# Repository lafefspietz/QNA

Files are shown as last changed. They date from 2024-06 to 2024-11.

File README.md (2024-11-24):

# [Quantum Network Analyzer](https://github.com/lafefspietz/QNA/)

System for calibrated high throughput microwave scattering parameter measurement using quantum standards.

Microwave lines are expensive.  Dil fridges are expensive.  Adding cryogenic RF switches to a system can be a force multiplier for both microwave measurement infrastructure and cryogenic infrastructure, multiplying up the number of chips which can be measured per cool down by however many RF lines the switch network adds. 

The system documented here turns one RF line into 9 by taking a single RF input, using switches to split between 9 quantum samples, and then a second switch network which feeds a single RF output. A mechanical assembly with COTS cryogenic RF devices will allow for measuring all 4 scattering parameters with a single RF in and RF output.  

Calibration software which can use a standard qubit chip to measure test chips will be part of the system.  An Arduino-based rack mount controller is part of the system as well.

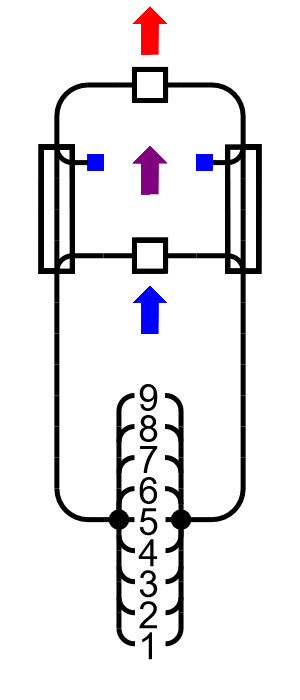
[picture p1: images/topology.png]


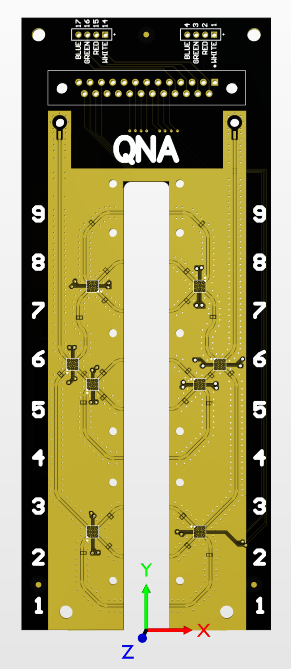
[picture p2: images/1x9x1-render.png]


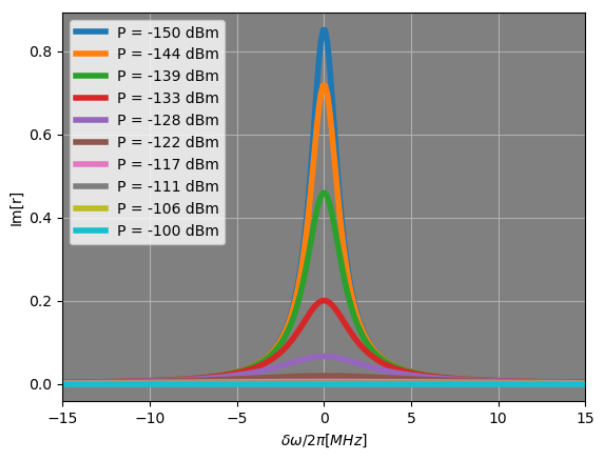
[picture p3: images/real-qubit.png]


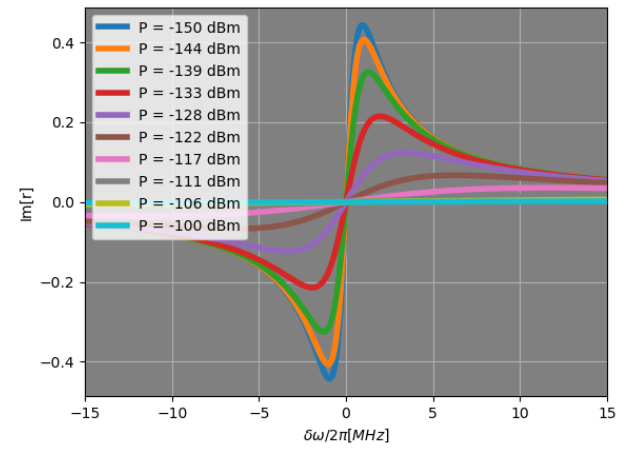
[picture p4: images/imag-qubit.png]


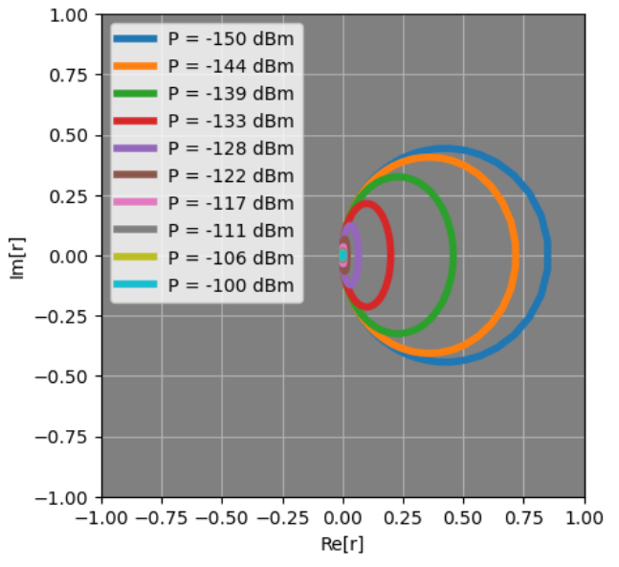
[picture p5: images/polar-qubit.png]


## System Elements

 - Wood board to fit in 19 inch rack
 - Control panel circuit board
 - 3d printed parts to connect circuit boards to wood board
 - Custom machined aluminum box to contain 90 volt electronics
 - DSUB to Fischer cable to connect to dil fridge
 - Arduino Mega 
 - Arduino Mega shield circuit board and components
 - DC DC converter built from COTS circuits
 - Relay control board with pull down resistors which selects which DC lines are energized with 90 volts
 - 1x9x1 switch board which puts 9 quantum devices in a single cryogenic RF line
 - Mounting bracket for COTS cryogenic RF components
 - Collection of COTS cryogenic RF components which bold to the above bracket
 - Sample enclosure
 - Outer sample box lid with small opening for changing samples and wire bonding
 - Inner sample box lid over sample opening
 - Standard qubit chips of different sizes
 - Arduino control code
 - Python control code
 - Calibration method based on tunable qubit chips to determine both scattering parameter calibration and noise calibration

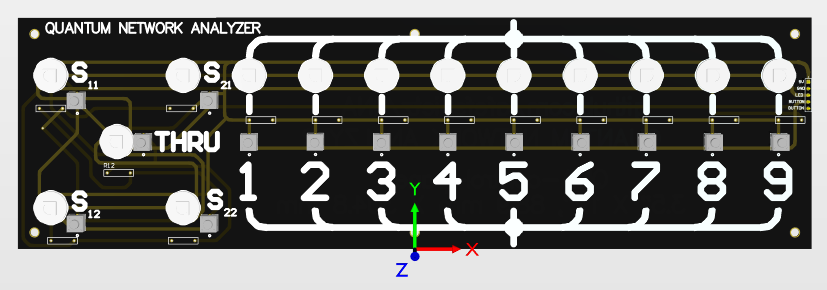
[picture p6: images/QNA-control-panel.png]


 - [14X pixels Flora RGB Smart NeoPixel version 3 - Sheet of 20](https://www.adafruit.com/product/1559)
 - [14X SPST tactile switch, E-Switch part number TL59NF160Q](https://www.digikey.com/en/products/detail/e-switch/TL59NF160Q/390533)
 - [1X 5 wire cables](https://www.amazon.com/StarTech-USBINT5PIN-Internal-Motherboard-Header/dp/B003HHROBG/)
 - [14X 10 k 0.1% axial reistors, Yageo part number MFP-25BRD52-10K](https://www.digikey.com/en/products/detail/yageo/MFP-25BRD52-10K/2058797)

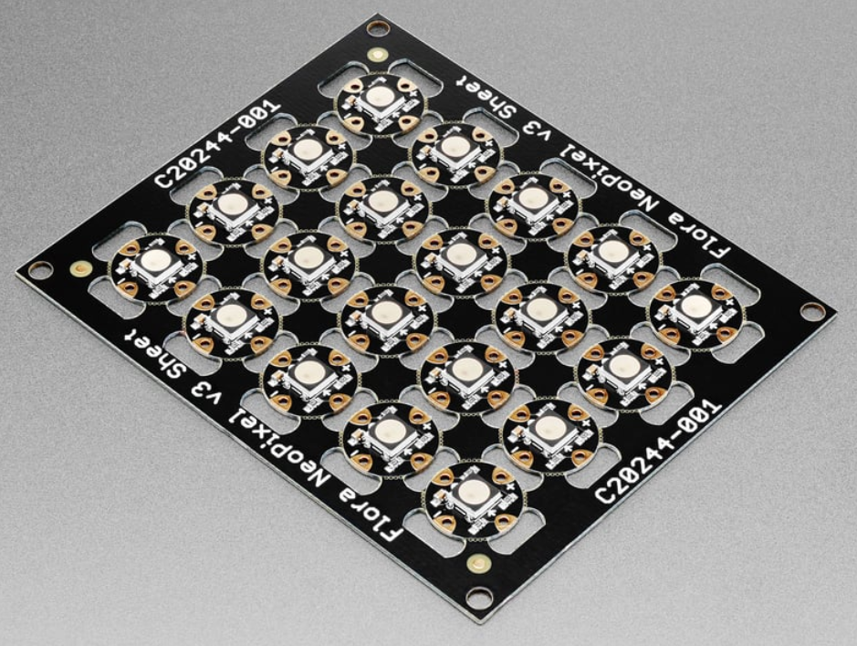
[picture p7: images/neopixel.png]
(https://www.adafruit.com/product/1559)


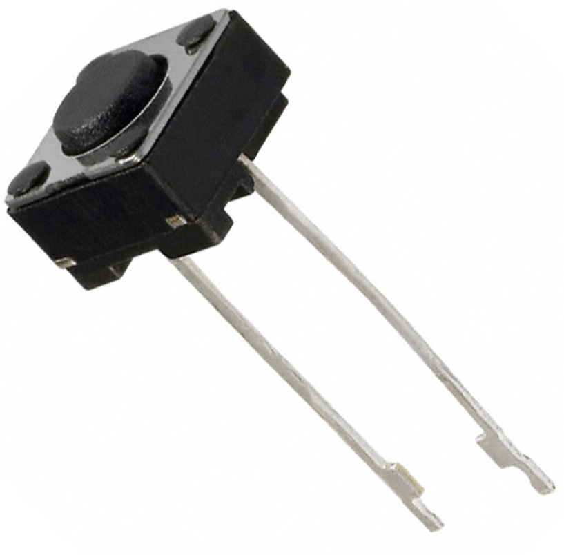
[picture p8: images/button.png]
(https://www.digikey.com/en/products/detail/e-switch/TL59NF160Q/390533)


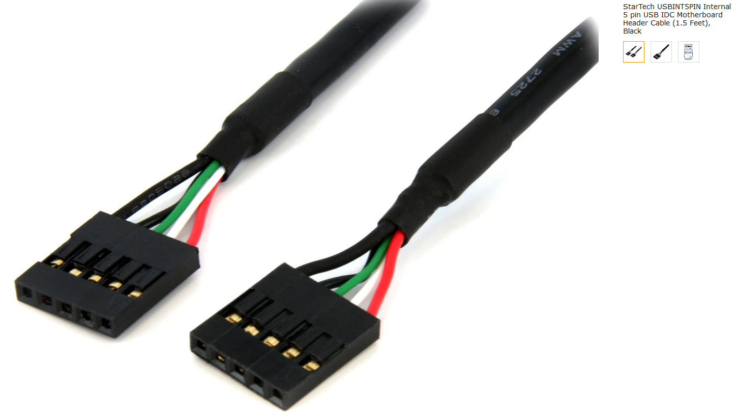
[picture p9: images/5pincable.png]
(https://www.amazon.com/StarTech-USBINT5PIN-Internal-Motherboard-Header/dp/B003HHROBG/)


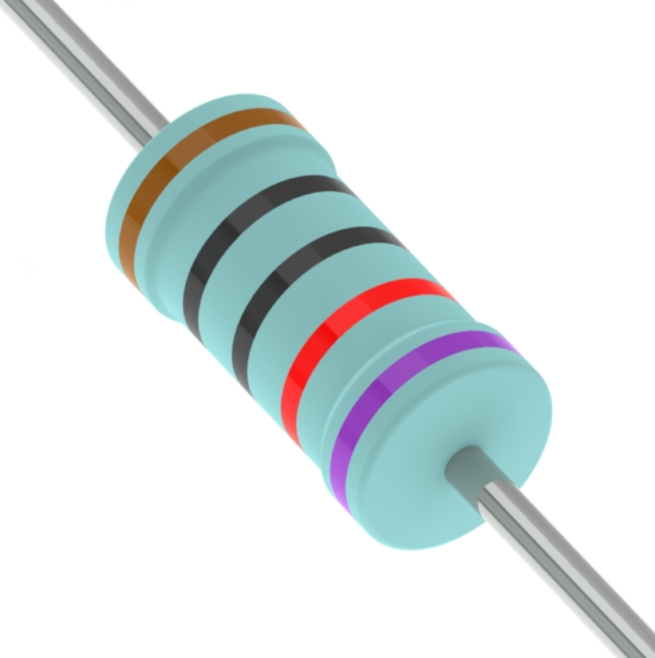
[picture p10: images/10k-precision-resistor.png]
(https://www.digikey.com/en/products/detail/yageo/MFP-25BRD52-10K/2058797)


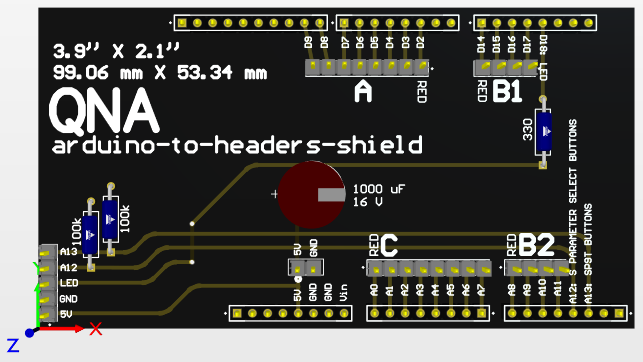
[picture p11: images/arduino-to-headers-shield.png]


 - [arduino-to-headers-shield-gerberes.zip](arduino-to-headers-shield-gerberes.zip)
 - [1000 uF 16 V electrolytic capacitor, Rubycon part number 16PK1000MEFC10X12.5](https://www.digikey.com/en/products/detail/rubycon/16PK1000MEFC10X12-5/3563556)
 - [100 kOhm Stackpole Electronics part number RNF14FTD100K](https://www.digikey.com/en/products/detail/stackpole-electronics-inc/RNF14FTD100K/1706591)
 - [330 Ohm Stackpole Electronics part number CF18JT330R](https://www.digikey.com/en/products/detail/stackpole-electronics-inc/CF18JT330R/1741683)
 - [0.1 inch header strips](https://www.amazon.com/Header-Lystaii-Pin-Connector-Electronic/dp/B06ZZN8L9S/)

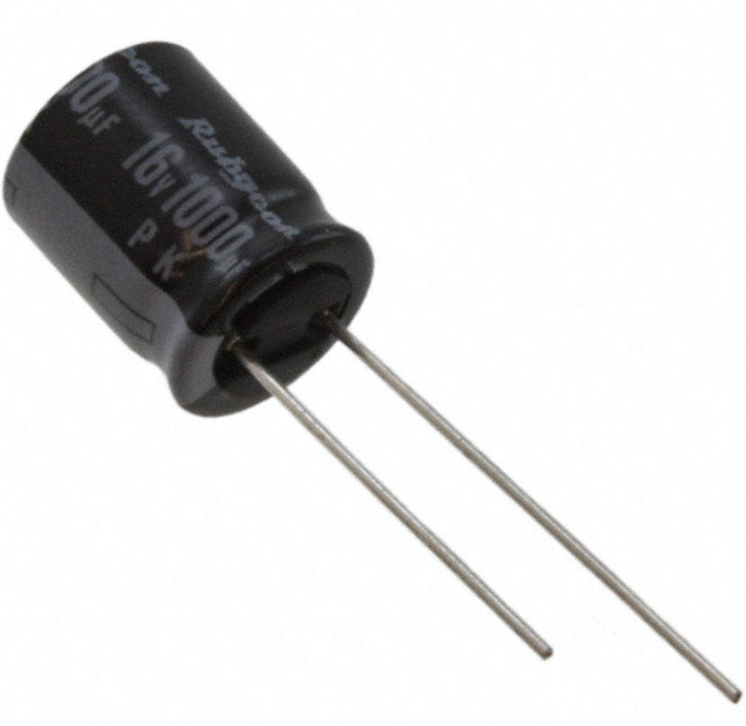
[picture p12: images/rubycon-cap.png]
image of electrolytic capacitor (https://www.digikey.com/en/products/detail/rubycon/16PK1000MEFC10X12-5/3563556)


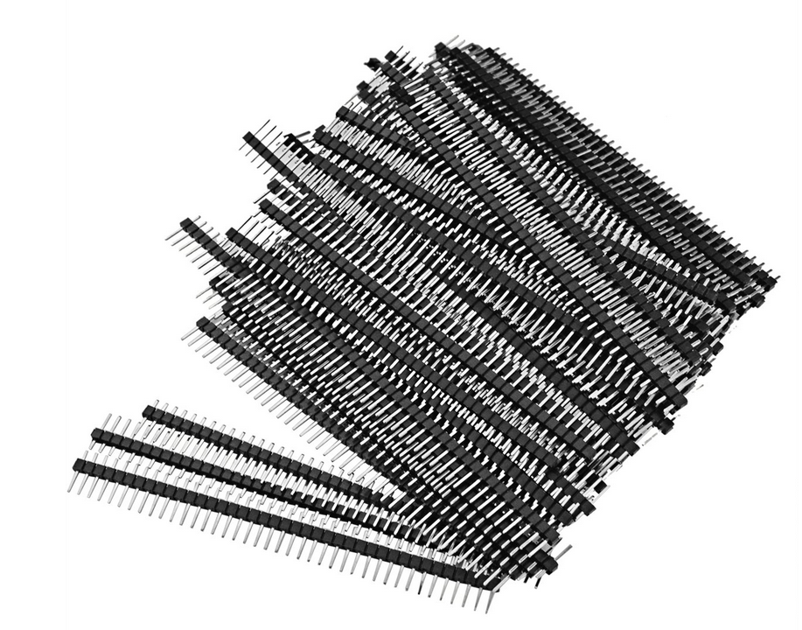
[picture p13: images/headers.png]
[]

Add link here to the 4 and 8 pin cables which connect these boards

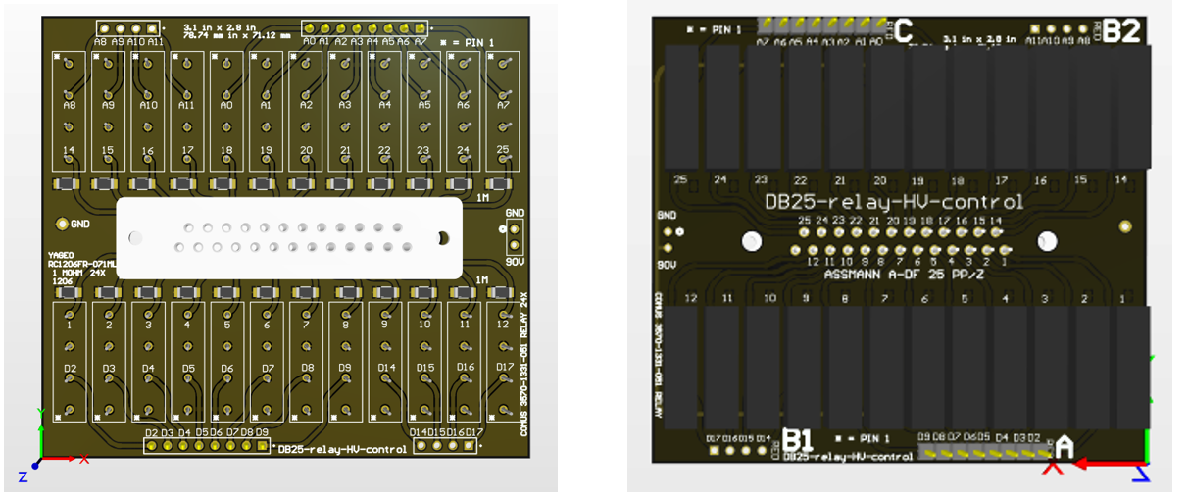
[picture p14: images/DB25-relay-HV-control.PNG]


 - [DB25-relay-HV-control-gerbers.zip](DB25-relay-HV-control-gerbers.zip)
 - [DB25-relay-HV-control-gerbers.PcbDoc](DB25-relay-HV-control-gerbers.PcbDoc)
 - [DB25-relay-HV-control-gerbers.PrjPcb](DB25-relay-HV-control-gerbers.PrjPcb)
 - [DB25-relay-HV-control-gerbers.](DB25-relay-HV-control-gerbers.PrjPcbStructure)
 - [DB25-relay-HV-control-gerbers.](DB25-relay-HV-control-gerbers.SchDoc)
 - [24 x 5 volt relay, Comus International part number 3570-1331-053](https://www.digikey.com/en/products/detail/comus-international/3570-1331-053/7497099)
 - [24x 1 MOhm resistor in SMT 1206 package, Yageo part number RC1206FR-071ML](https://www.digikey.com/en/products/detail/yageo/RC1206FR-071ML/728388)
 - [1x Board mount female DB-25 connector, Assmann part number A-DF 25 PP/Z](https://www.digikey.com/en/products/detail/assmann-wsw-components/A-DF-25-PP-Z/1241794)
 - [0.1 inch header strips](https://www.amazon.com/Header-Lystaii-Pin-Connector-Electronic/dp/B06ZZN8L9S/)

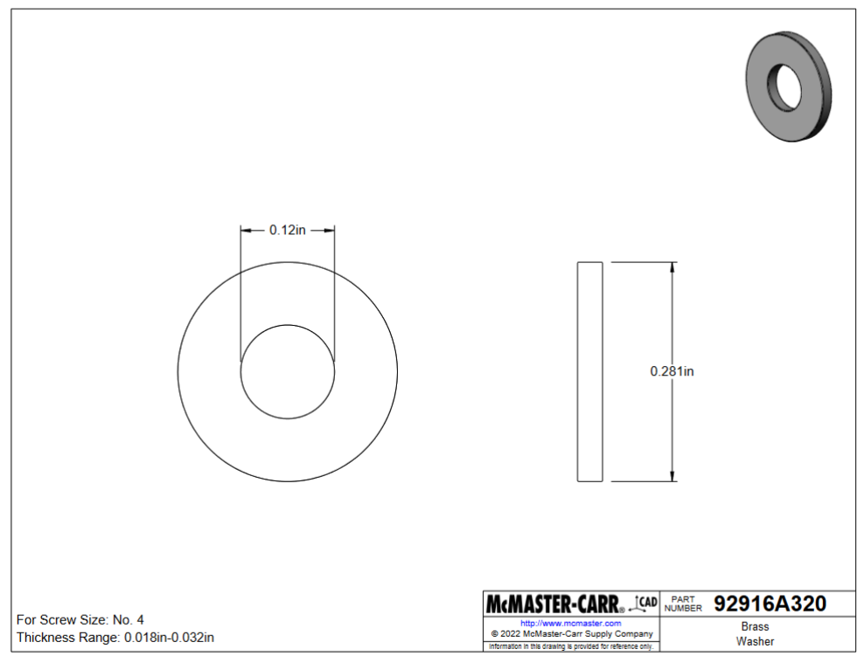
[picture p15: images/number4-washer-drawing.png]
(https://www.mcmaster.com/92916a320/)


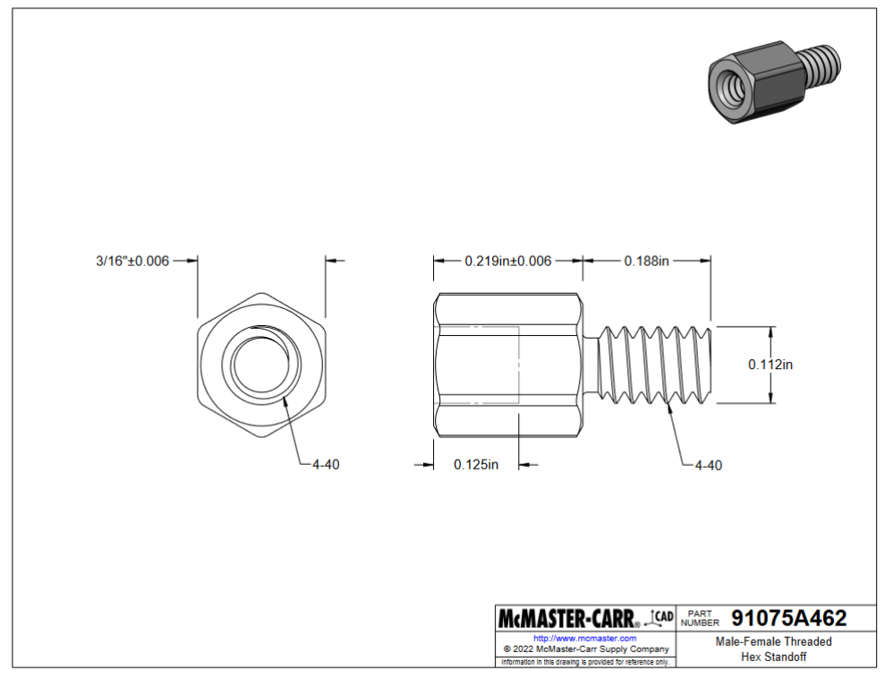
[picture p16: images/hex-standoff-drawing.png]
(https://www.mcmaster.com/91075A462/)


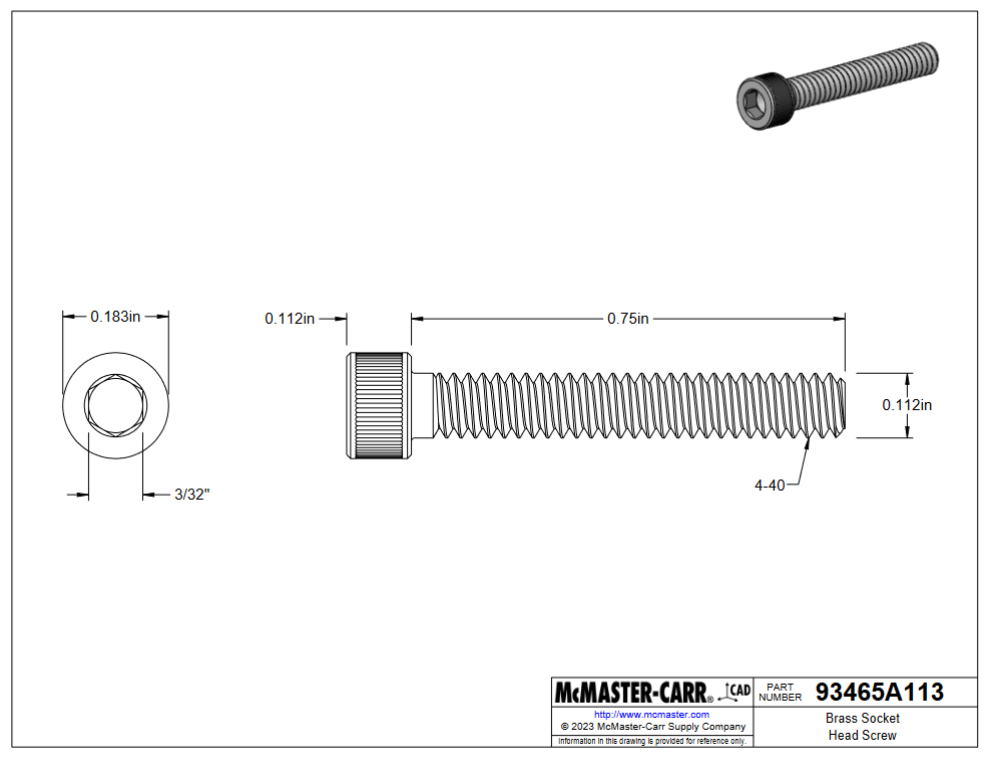
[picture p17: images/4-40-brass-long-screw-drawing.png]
(https://www.mcmaster.com/93465a113/)


# 1x9x1



 - [microd](https://www.digikey.com/en/products/detail/cinch-connectivity-solutions/M83513-25-D01CP/12471446)
 - [2 mm headers](https://www.digikey.com/en/products/detail/te-connectivity-amp-connectors/2-292161-4/5124519)
 - [MEMS switch](https://www.mouser.com/new/menlo-micro/menlo-micro-mm5130-sp4t-rf-switch/)
 - [56 k resistor](https://www.digikey.com/en/products/detail/te-connectivity-passive-product/CPF0201B56K2E1/14007085)
 - [SMP connectors from Molex](https://www.digikey.com/en/products/detail/molex/0853050232/2421464)

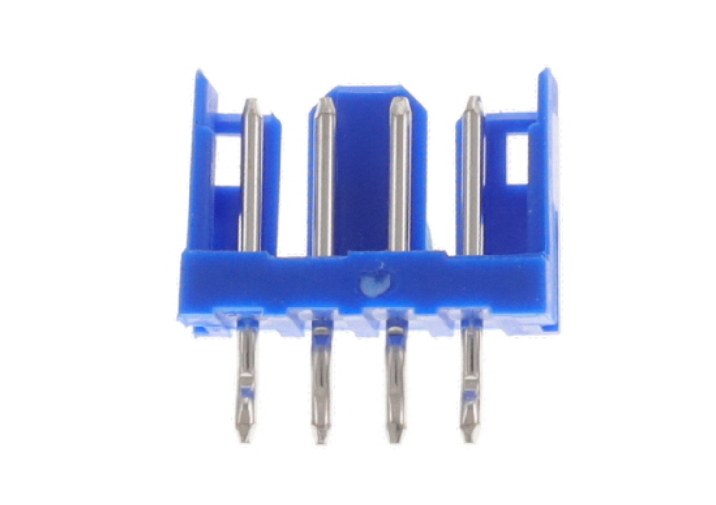
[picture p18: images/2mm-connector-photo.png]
2mm 4 pin connector (https://www.digikey.com/en/products/detail/te-connectivity-amp-connectors/2-292161-4/5124519)


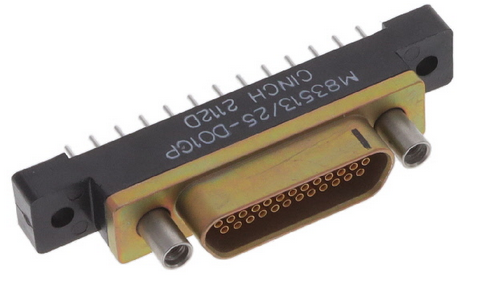
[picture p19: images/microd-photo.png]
(https://www.digikey.com/en/products/detail/cinch-connectivity-solutions/M83513-25-D01CP/12471446)


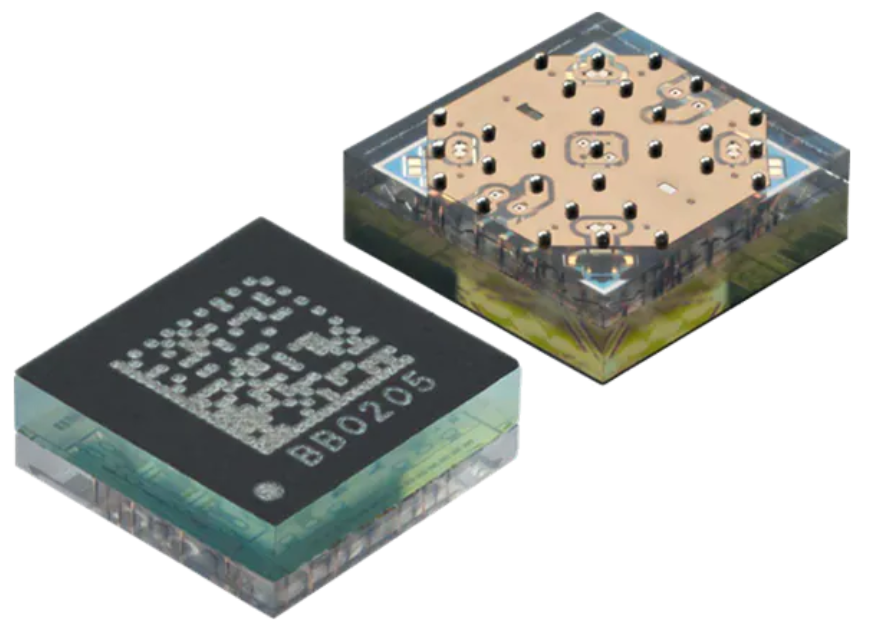
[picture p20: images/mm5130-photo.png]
(https://www.mouser.com/new/menlo-micro/menlo-micro-mm5130-sp4t-rf-switch/)


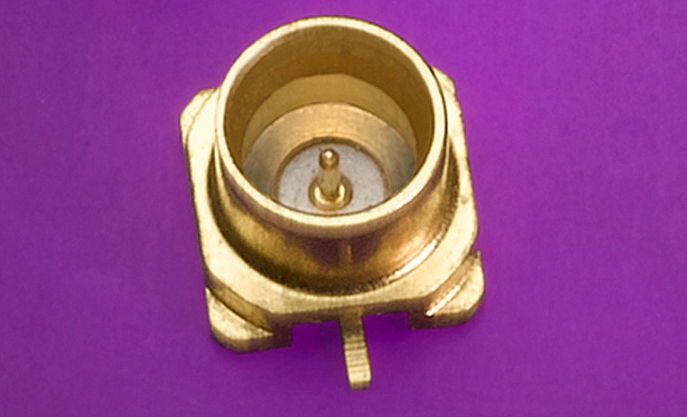
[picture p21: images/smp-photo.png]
(https://www.digikey.com/en/products/detail/molex/0853050232/2421464)


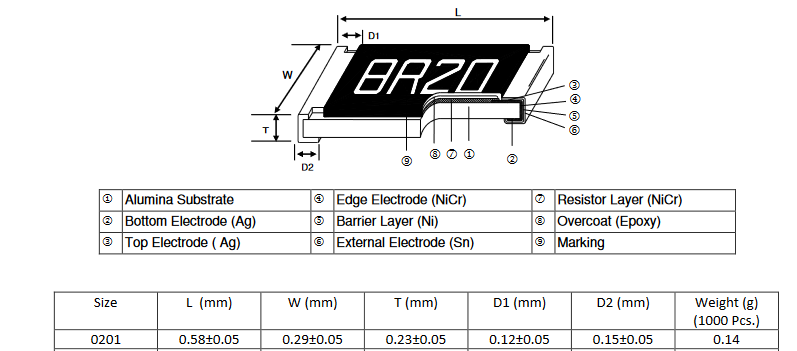
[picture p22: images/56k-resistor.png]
(https://www.digikey.com/en/products/detail/te-connectivity-passive-product/CPF0201B56K2E1/14007085)


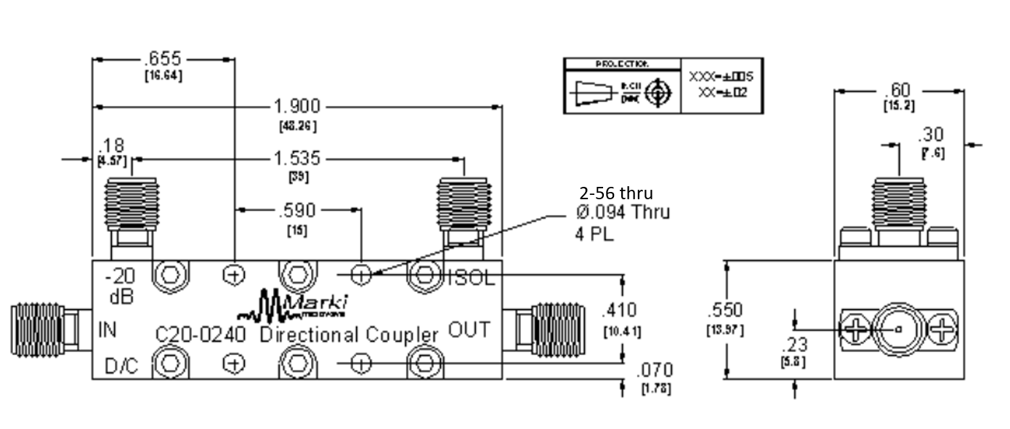
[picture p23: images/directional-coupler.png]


### [Marki Microwave C20-0240 Directional Coupler](https://markimicrowave.com/products/connectorized/directional-couplers/c20-0240/)

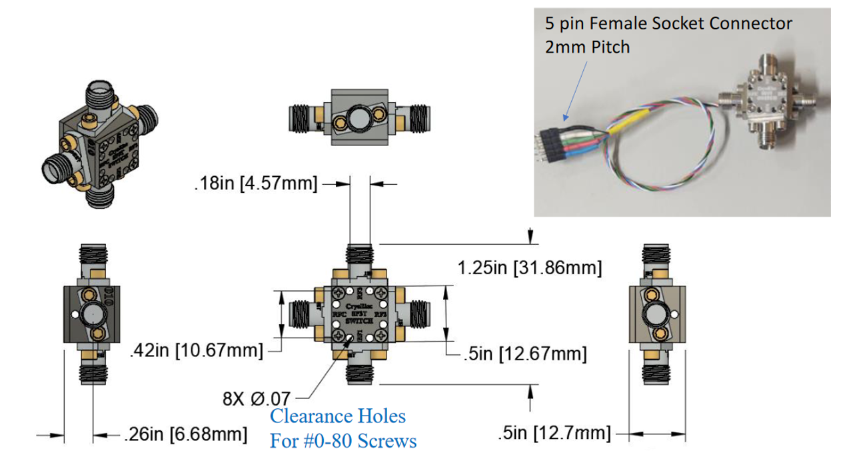
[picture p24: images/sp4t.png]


### [CryoElec SP3T coaxial switch](https://www.cryoelec.com/products/cryoswitchsp3t)

Versions can be constructed for 5 mm chips, 5.06 mm chips, 7.5 mm chips, 10 mm chips, and SMP connectors to break out to external devices.

Install [xampp](https://www.apachefriends.org/).

Install [Anaconda](https://docs.anaconda.com/anaconda/install/)

Open an anaconda prompt and type the following 

```
jupyter notebook --notebook-dir=c:\xampp\htdocs\quantumswitch
```

## 1x9x1 System Elements



### 1x9x1 PCB, RF Pool with RO4350

### [Eurocircuits RF Pool link](https://www.eurocircuits.com/pcb-assembly-rf-pool/)



## 2X

### [TE Connectivity 2-292161-4 CONN HEADER VERT 4POS 2MM](https://www.digikey.com/en/products/detail/te-connectivity-amp-connectors/2-292161-4/5124519)



## 2X

### [Molex 085305-0232 SMT SMP connector](https://www.digikey.com/en/products/detail/molex/0853050232/2421464)



## 1X

### [Cinch Connectivity Solutions M83513/25-D01CP 25 pin microD board mount connector](https://www.digikey.com/en/products/detail/cinch-connectivity-solutions/M83513-25-D01CP/12471446)



## 8X

### [Menlo Micro MM5130-03NDB-TR RF Switch ICs DC-26GHz - SP4T - 2.5 mm x 2.5 mm 29 pin](https://mou.sr/4fuziKD)



### 24X

### [TE Connectivity CPF0201B56K2E1  56 k Ohm 0201 surface mount resistor](https://www.digikey.com/en/products/detail/te-connectivity-passive-product/CPF0201B56K2E1/14007085)

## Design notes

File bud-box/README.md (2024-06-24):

## [Back to Main QNA](../)

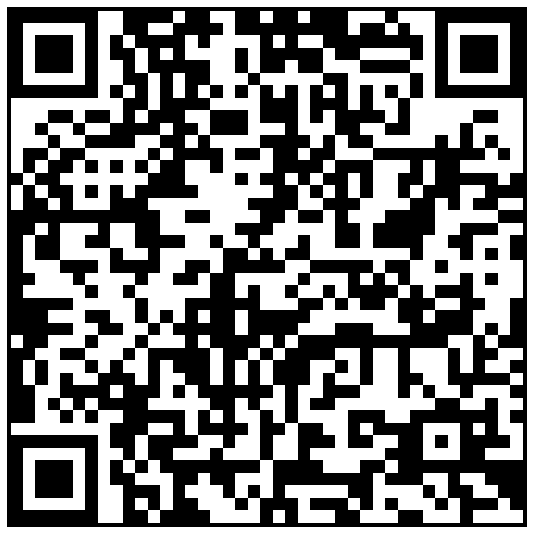
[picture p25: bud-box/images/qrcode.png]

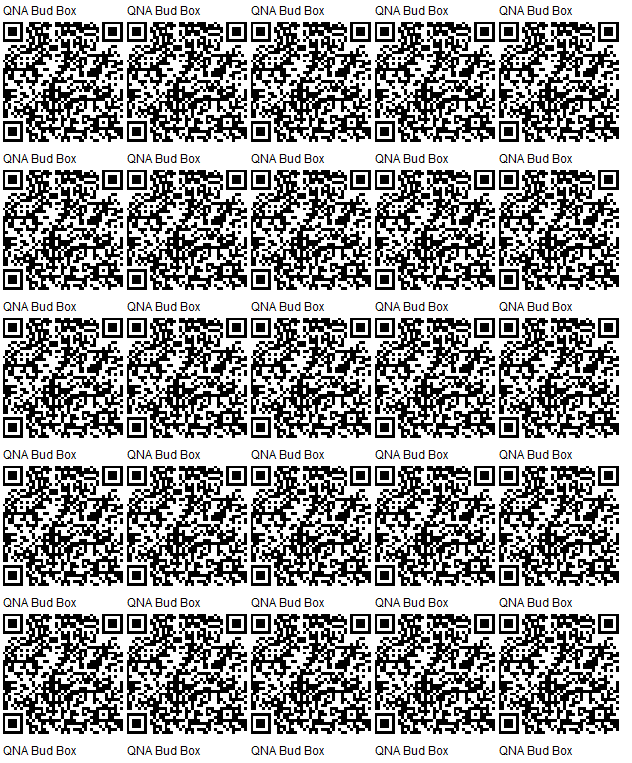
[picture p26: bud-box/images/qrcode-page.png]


# [Bud Box](https://github.com/lafefspietz/QNA/tree/main/bud-box)

We use a diecast aluminum enclosure from [Bud Industries](https://www.budind.com/)(part number [AN-1304-A](https://www.budind.com/product/nema-ip-rated-boxes/an-a-series-style-a-aluminum-enclosure/an-1304/)) to enclose the high voltage driver for the MEMS switches used in the QNA system. 

This box can be modified yourself if you have access to a milling machine or you can get it modified by Bud or by some third party machine shop.  

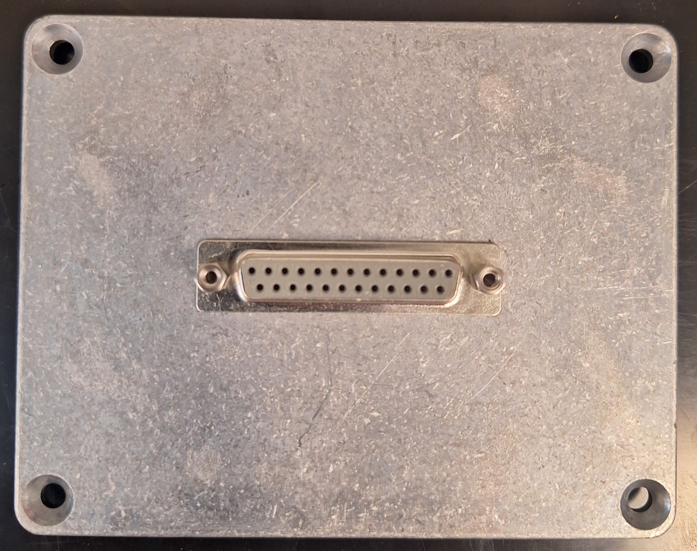
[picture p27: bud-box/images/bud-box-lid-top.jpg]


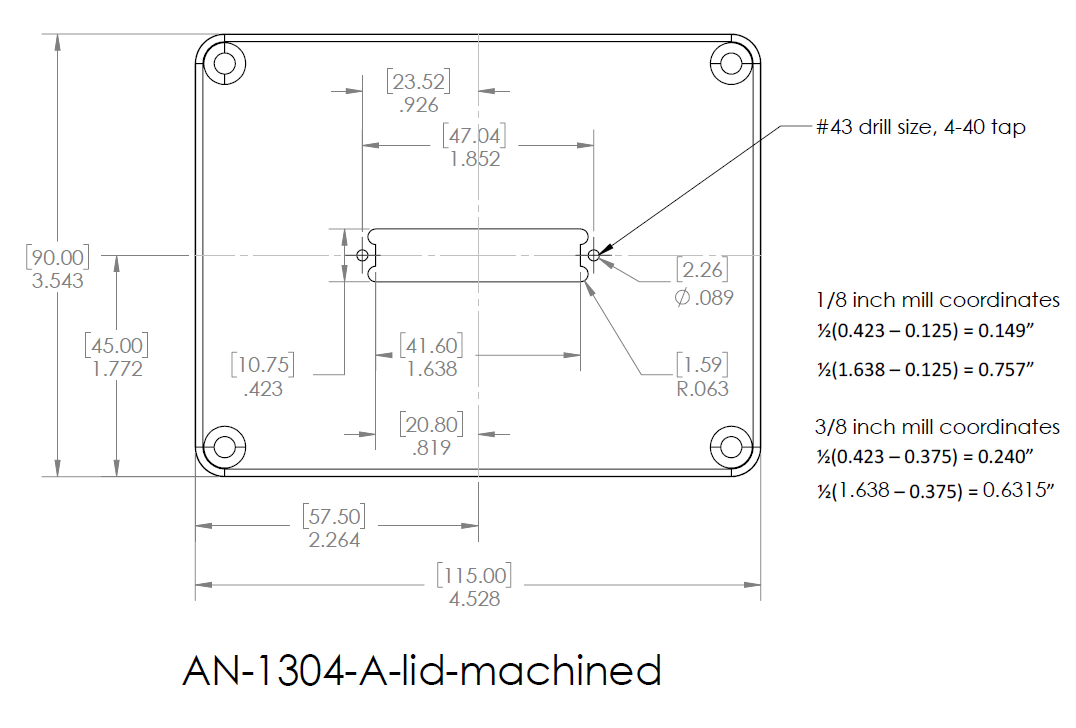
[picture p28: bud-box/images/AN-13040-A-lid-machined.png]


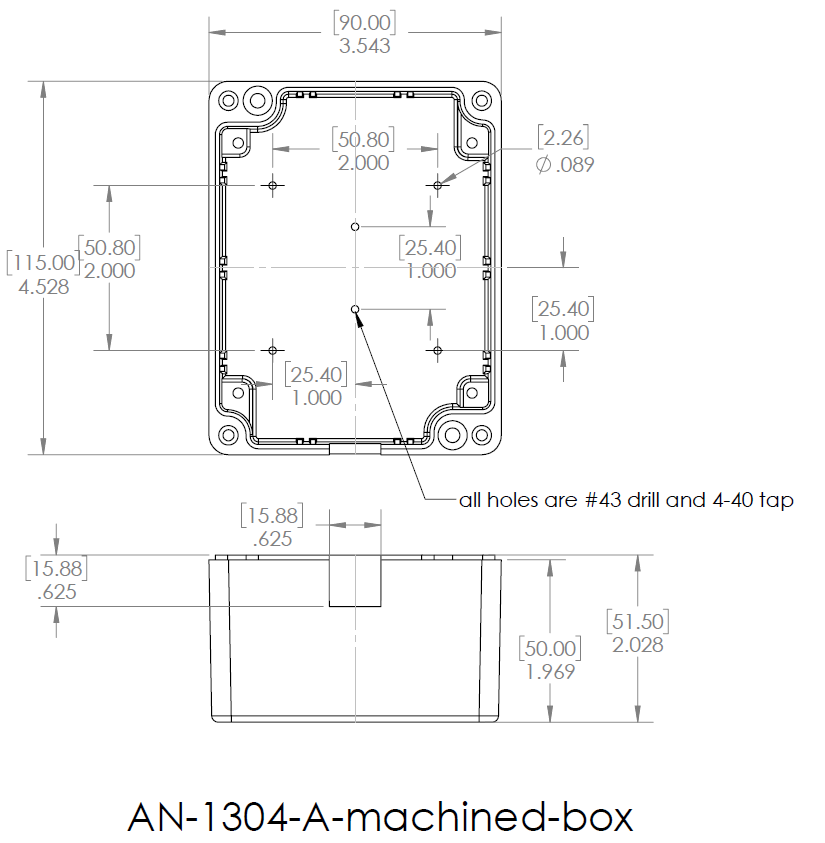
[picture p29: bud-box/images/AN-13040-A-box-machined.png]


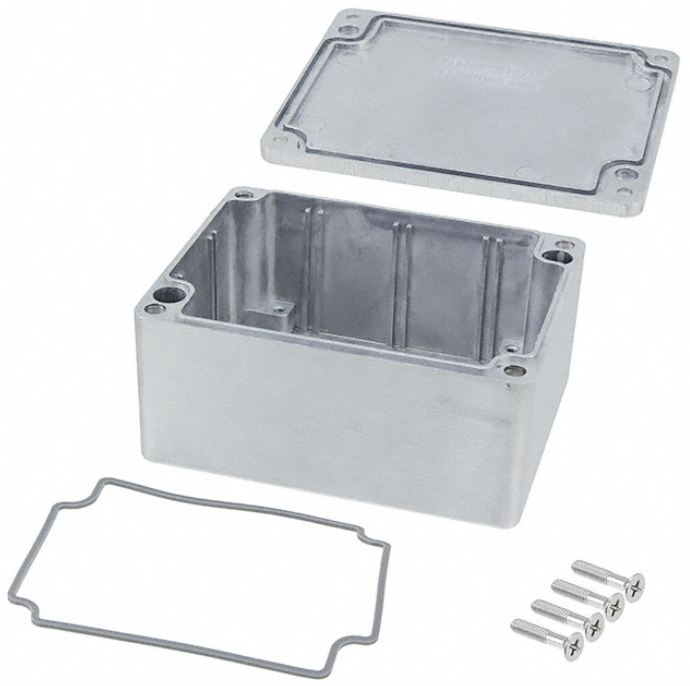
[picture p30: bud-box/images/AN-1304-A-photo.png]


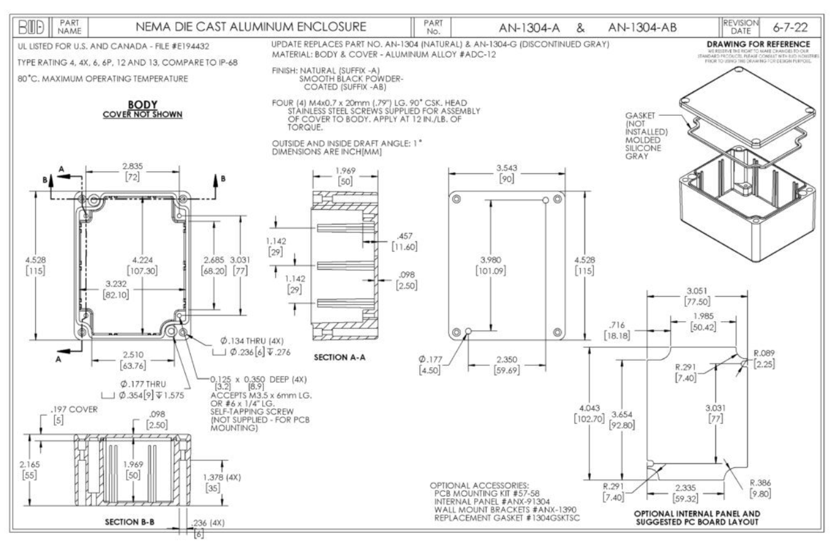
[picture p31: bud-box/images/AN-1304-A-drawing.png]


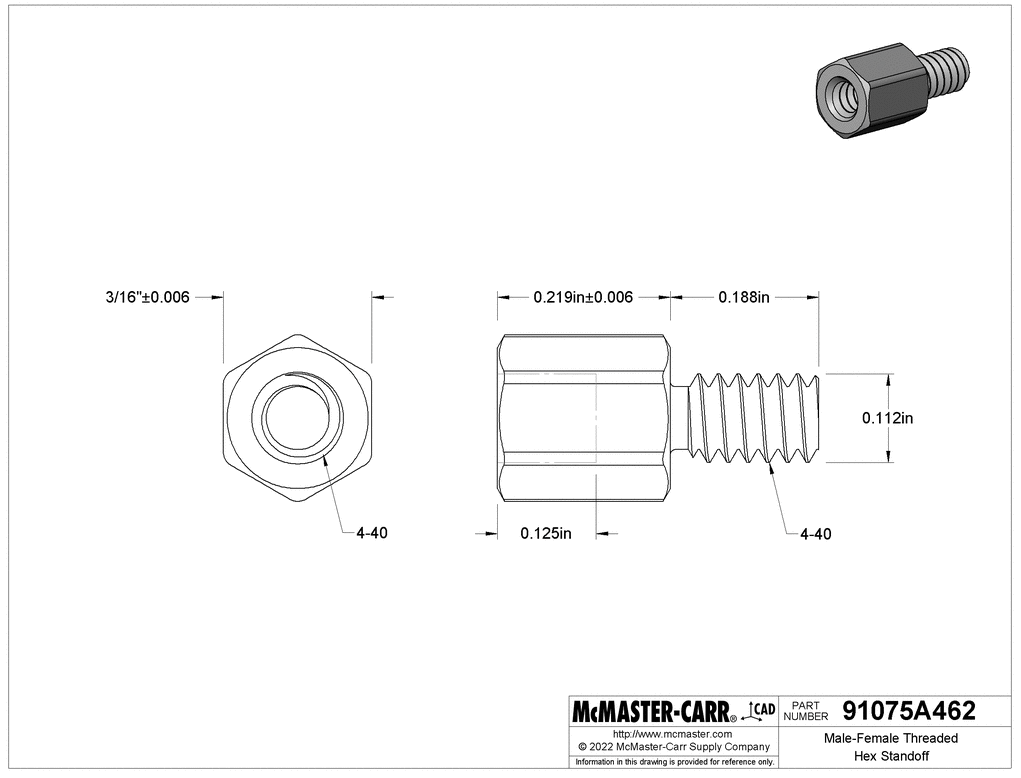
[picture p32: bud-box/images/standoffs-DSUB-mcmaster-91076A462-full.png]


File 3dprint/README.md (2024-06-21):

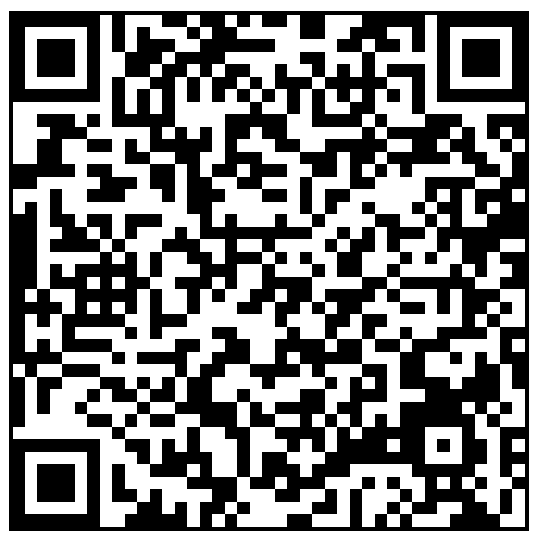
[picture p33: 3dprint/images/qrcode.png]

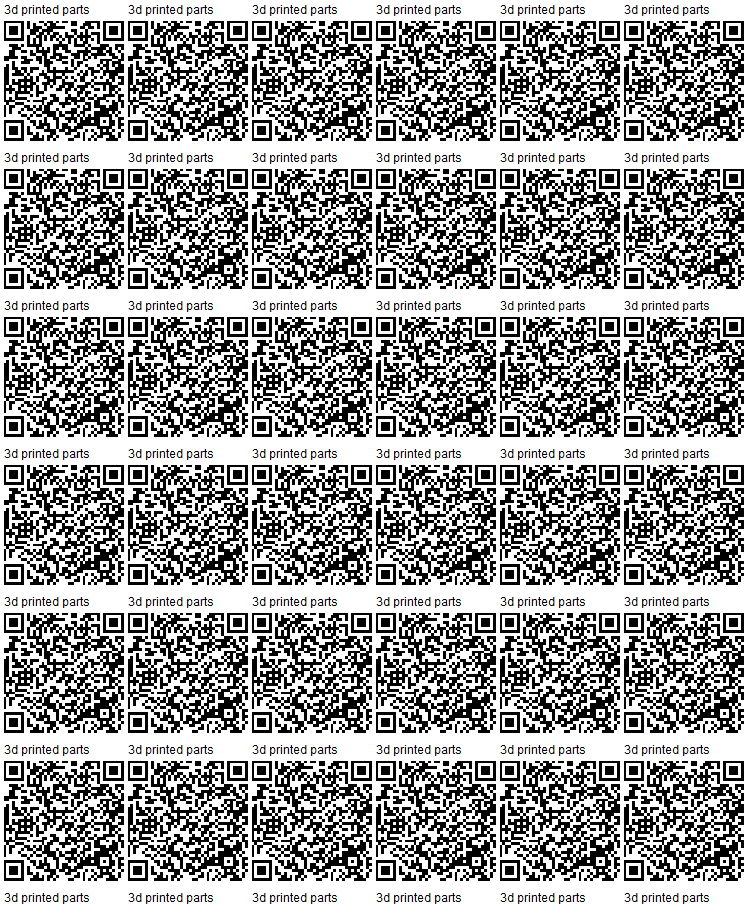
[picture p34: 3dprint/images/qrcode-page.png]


# [3d Printed Parts]()

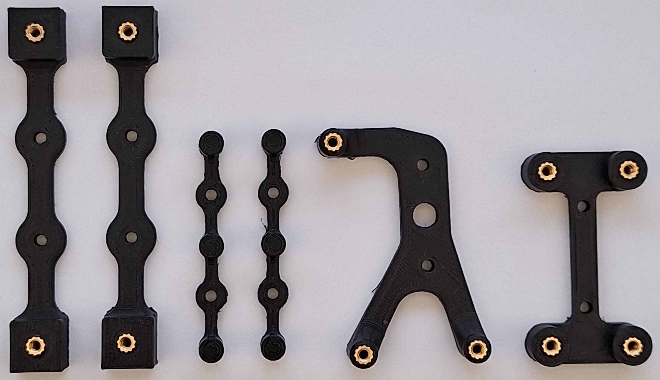
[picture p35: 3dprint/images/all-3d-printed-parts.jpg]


 1. [front-panel-edge-bracket.STL, print 2, add inserts](front-panel-edge-bracket.STL)
 2. [front-panel-center-bracket.STL, print 2](front-panel-center-bracket.STL)
 3. [arduino-bracket.STL, print 1, add inserts](arduino-bracket.STL)
 4. [HV-DCDC-bracket.STL, print 1, add inserts](HV-DCDC-bracket.STL) 

## Thread Inserts

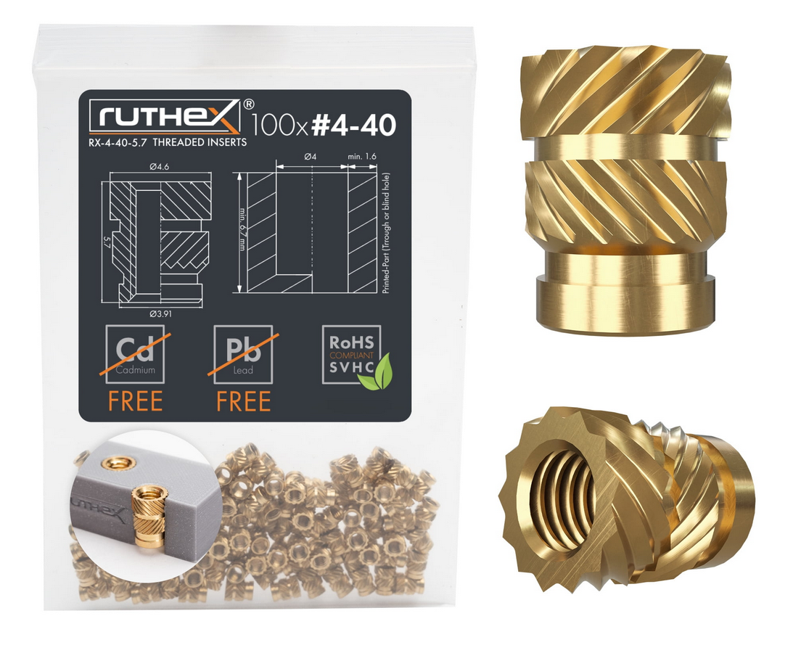
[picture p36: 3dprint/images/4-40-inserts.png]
(https://www.3djake.com/ruthex/threaded-insert-4-40-unc-100-pieces)


## 4-40 Quarter Inch Screws

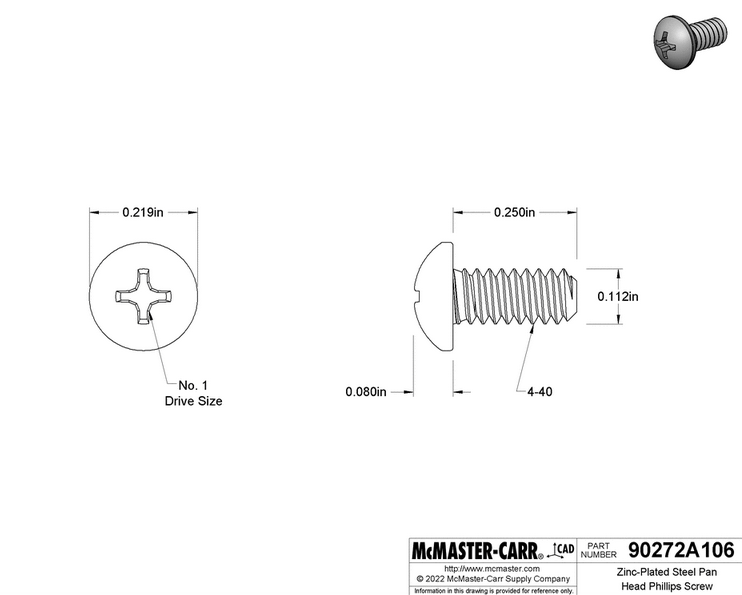
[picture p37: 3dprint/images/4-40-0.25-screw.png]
(https://www.mcmaster.com/90272A106/)


## #4 Wood Screws

[Mcmaster-Carr Part number 98685A540](https://www.mcmaster.com/98685A540/)

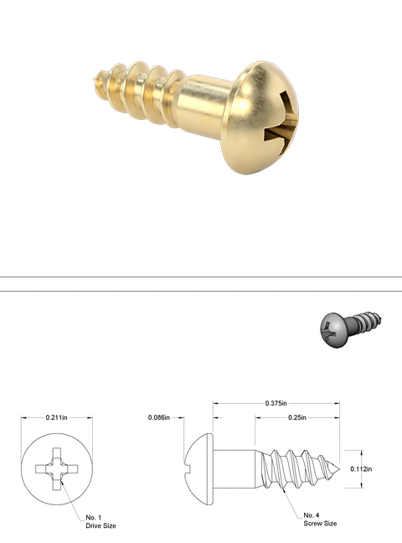
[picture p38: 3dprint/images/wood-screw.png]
(https://www.mcmaster.com/98685A540/)


## Arduino Bracket

Print one of these per controller.  This works for both Arduino UNO and Arduino Mega. Screw into wood using #4 wood screws.  

Use 4-40 brass thread inserts, press them in with a soldering iron. 

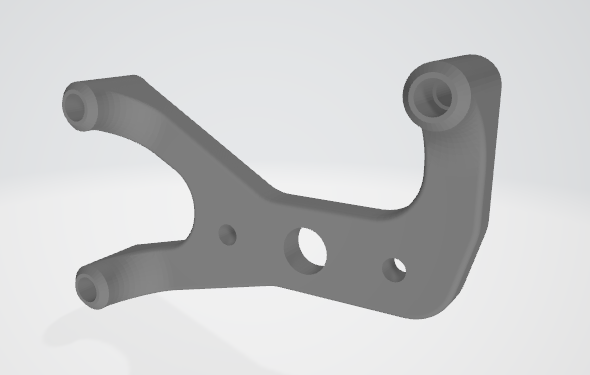
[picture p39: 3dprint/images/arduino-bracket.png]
arduino-bracket.STL
 

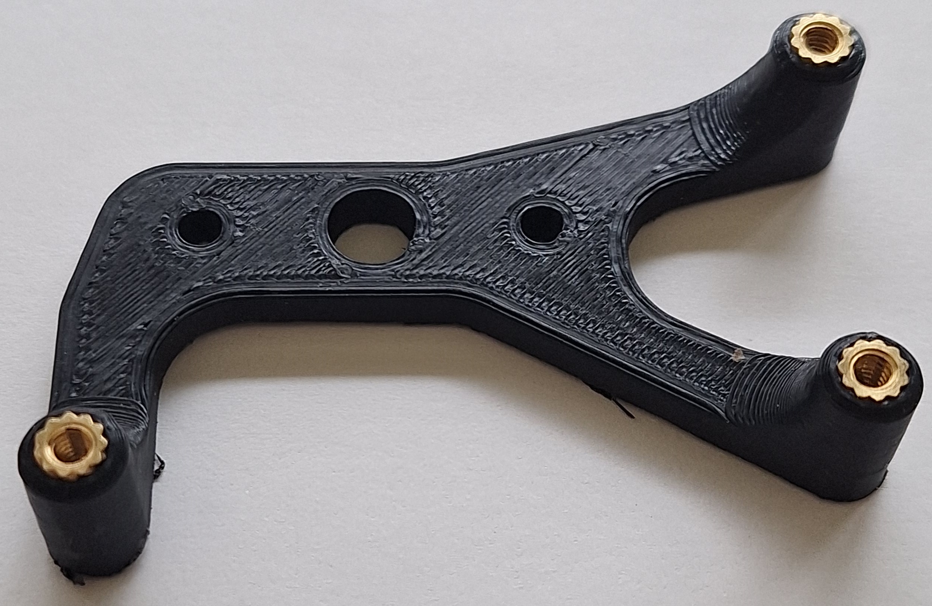
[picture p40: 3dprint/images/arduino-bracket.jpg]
arduino-bracket.STL
 

## DC DC converter Bracket

Use 4-40 brass thread inserts, press them in with a soldering iron

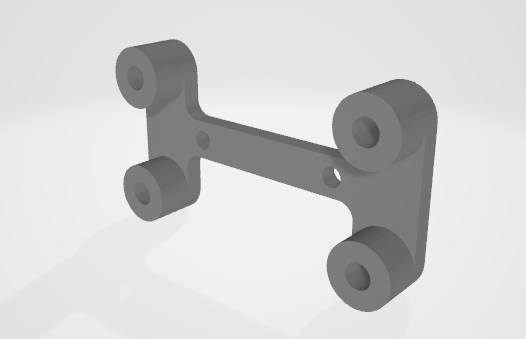
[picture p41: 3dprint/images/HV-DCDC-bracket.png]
HV-DCDC-bracket.STL
 

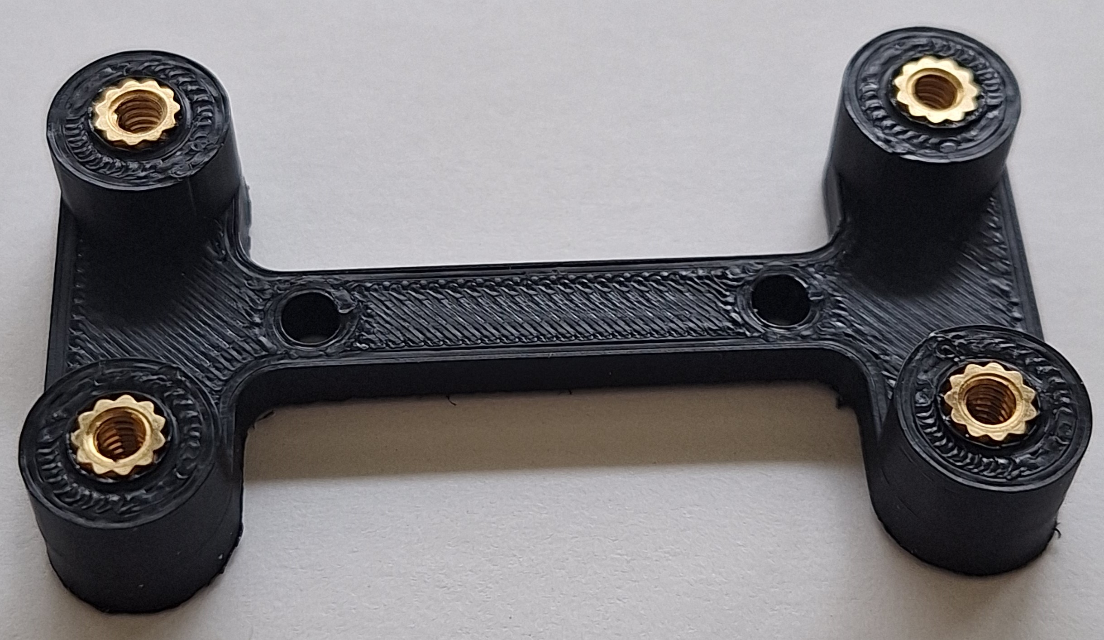
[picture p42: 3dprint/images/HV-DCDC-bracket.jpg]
HV-DCDC-bracket.STL


## Front Panel Edge Bracket

Use 4-40 brass thread inserts, press them in with a soldering iron. Attach to wood with #4 wood screws. 

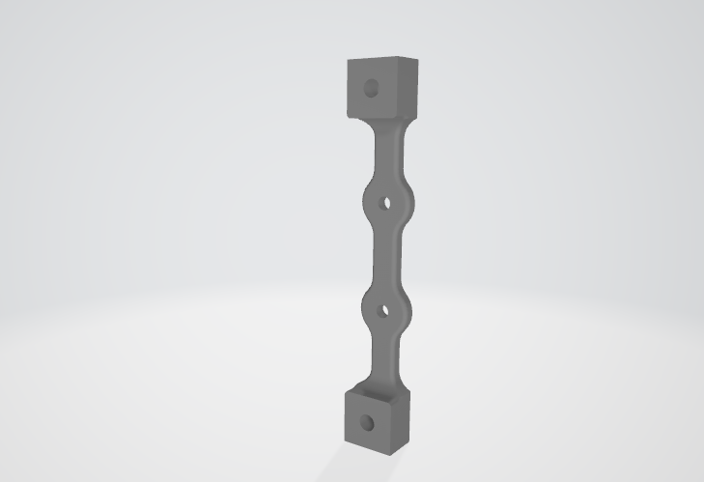
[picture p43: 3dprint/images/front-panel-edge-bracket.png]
front-panel-edge-bracket.STL
 

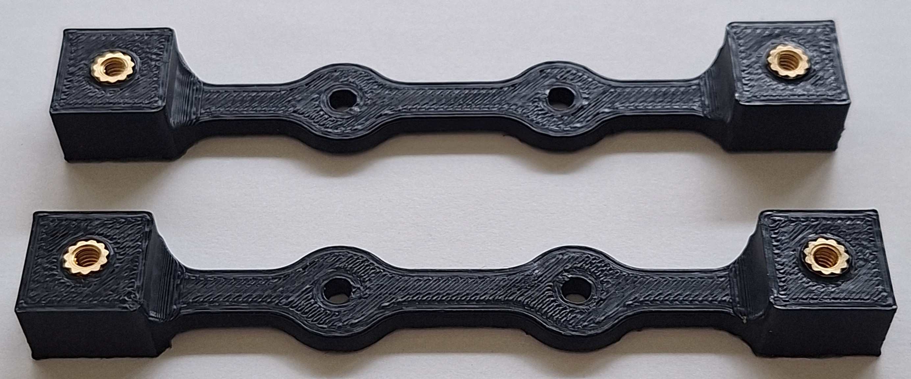
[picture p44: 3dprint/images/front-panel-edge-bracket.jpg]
front-panel-edge-bracket.STL
 

## Front Panel Center Bracket

place in center area of circuit board to prevent bowing, use #4 wood screws to mount.

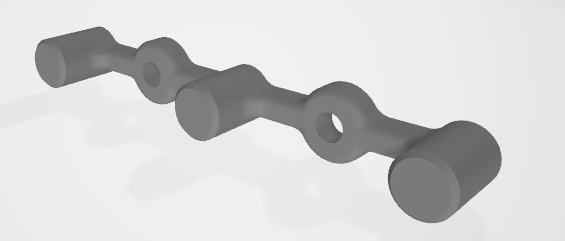
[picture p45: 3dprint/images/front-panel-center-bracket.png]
front-panel-center-bracket.STL
 

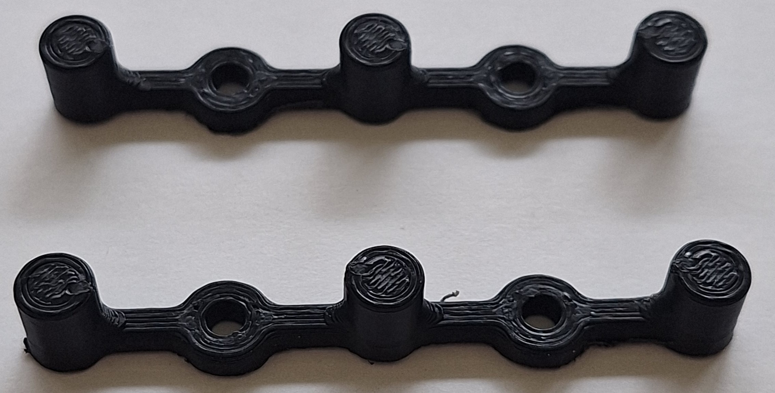
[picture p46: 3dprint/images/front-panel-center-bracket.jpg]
front-panel-center-bracket.STL
 

## Arduino UNO Hole Pattern

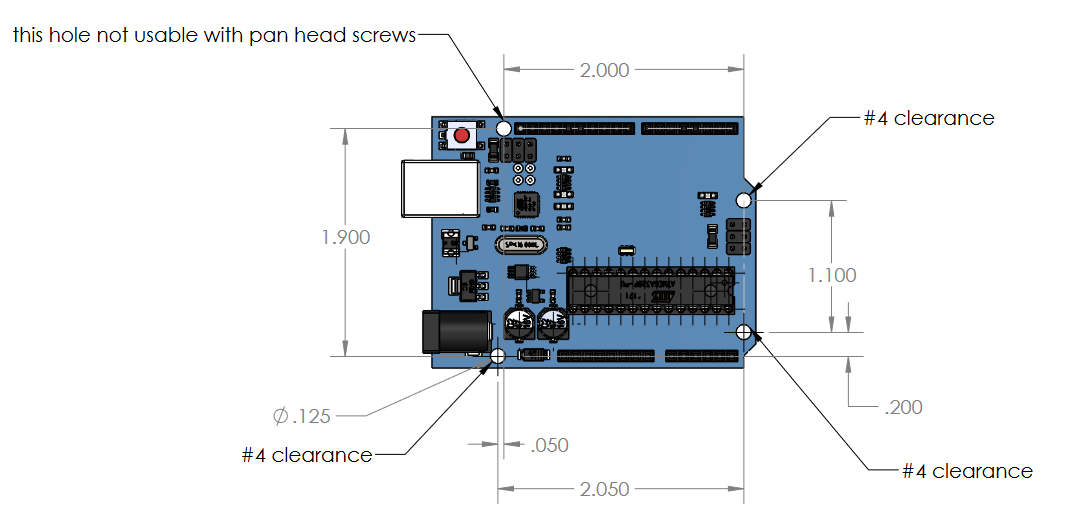
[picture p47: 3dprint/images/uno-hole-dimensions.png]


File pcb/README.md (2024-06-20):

# Printed Circuit Boards (PCB's)

## 9button-9neopixels

[9button-9neopixels/](9button-9neopixels/)

## arduno-to-headers-shield

## DB25-relay-HV-control

## microd-header-adapter-board-rev2

## rectangle11

## calboards

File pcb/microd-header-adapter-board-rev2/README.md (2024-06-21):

## [Up to PCB/](../)

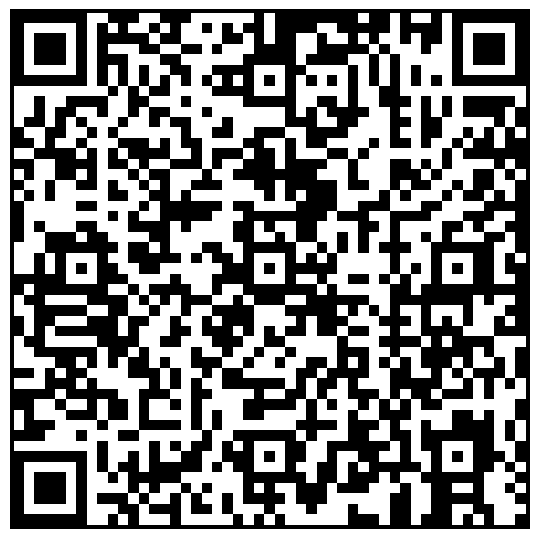
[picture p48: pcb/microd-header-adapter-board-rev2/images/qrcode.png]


 
 
# microd-header-adapter-board-rev2 Printed Circuit Board(PCB)



## Bill of Materials



 - [PCB's](https://www.pcbway.com)
 - [female micro D]()
 - [header strips (40 pins)](https://www.digikey.com/en/products/detail/amphenol-cs-commercial-products/G800W268018EU/17083164)

## Files

 - [Altium Schematic .SchDoc](microd-header-adapter-board-rev2.schDoc)
 - [Altium project file .PrjPcb](microd-header-adapter-board-rev2.PrjPcb)
 - [Altium Pcb File .PcbDoc](microd-header-adapter-board-rev2.PrjPcb)
 - [.zip of Gerber files](microd-header-adapter-board-rev2-gerbers.zip)
 
## Assembly Notes

Threaded standoffs must be carefully ground off with a cutting wheel on a Dremmel tool.  See standoffs in connector closeup below:



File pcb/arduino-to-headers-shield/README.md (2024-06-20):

## [Up to PCB/](../)





# 9button-9neopixel Printed Circuit Board(PCB)













## Bill of Materials



 - [PCB's](https://www.pcbway.com)
 - [ Neopixels (9x)](https://www.adafruit.com/product/1559)
 - [10 k resistors (9x)](https://www.digikey.com/en/products/detail/yageo/MFR-25FBF52-10K/13219)
 - [4 pin header cable (1x)](https://www.amazon.com/ZYAMY-Dupont-Connector-Multicolor-Breadboard/dp/B0789F523N/)
 - [header strips (40 pins)](https://www.digikey.com/en/products/detail/amphenol-cs-commercial-products/G800W268018EU/17083164)
 - [buttons (9x)](https://www.digikey.com/en/products/detail/e-switch/TL59NF160Q/390533)

[Digkey Cart with everything but PCB's](https://www.digikey.com/short/jzc9cpp0)

## Files

 - [Altium Schematic .SchDoc](9button-9neopixel.schDoc)
 - [Altium project file .PrjPcb](9button-9neopixel.PrjPcb)
 - [Altium Pcb File .PcbDoc](9button-9neopixel.PrjPcb)
 - [.zip of Gerber files](9button-9neopixel-gerbers.zip)

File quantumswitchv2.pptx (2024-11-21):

## Notes on Open Source Quantum Switch version 2

## To do

- Add connectors for control of four throw switches
- Update the launch to the one copied from the launch test board
- Make the silk screen make sense, add all relevant information including url
- Add teardrop launches to rf lines on switches
- Add back the ground plane and vias
- Make the copper have a square end at board edges
- Go thru and align everything so it has maximal symmetry
- Make a version with internal ecal and six DUTs
- Move all the dc lines out of the way of the vias
- Make the dimensions all make sense, including the mounting holes

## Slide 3


2-56 thru

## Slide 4


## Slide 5


https://www.digikey.com/en/products/detail/te-connectivity-amp-connectors/2-292161-4/5124519

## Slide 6

## Anritsu K250 Bias tee


https://www.anritsu.com/en-us/components-accessories/products/k250-v250

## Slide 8


50

50

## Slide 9


https://www.amazon.com/Pzsmocn-Connector-Terminal-Electronic-Project/dp/B0BY8W5H71/

https://www.amazon.com/uxcell-Connector-Ribbon-Female-Length/dp/B07FLRW1ZL/

## DB25-relay-HV-control


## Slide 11


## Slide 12


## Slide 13


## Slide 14


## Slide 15

MICRO D: 25,12,24,11 | 23,10,22,9 | 21,8,20,7 | 19,6,18,5

U1 { G1, G4, G3, G2} | U4 {G1, G4, G3, G2} | U2 {G1, G4, G3, G2} U3 {G4, G3, G2, G1}

U8 {G2,G1,G4,G3} | U6 {G3,G2,G1,G4} | U7 {G2,G1,G4,G3} | U5 {G3,G2,G1,G4}

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
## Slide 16


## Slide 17


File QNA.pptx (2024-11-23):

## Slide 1

QUANTUM NETWORK ANALYZER


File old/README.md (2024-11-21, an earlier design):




# [Quantum Network Analyzer(QNA)](https://github.com/lafefspietz/QNA)

The QNA is an open source system of technologies used to measure how signals flow into and out of quantum microwave circuits. My "microwave" we generally mean from a few hundred megahertz to a few 10's of gigahertz.  And by "quantum" we mean that the temperature of the circuits is low enough that hf >> kT, where h is the Planck constant and k is the Boltzmann constant. 

Being in this quantum microwave regime means that we are generally dealing with temperatures about 10,000 times colder than room temperature, which are usually created using a [dilution refrigerator](https://en.wikipedia.org/wiki/Dilution_refrigerator). 

The components shared in this repository represent tools for using the MEMS-based "Ideal Switch" from Menlo Microwave to create RF calibration systems for use in a dilution refrigerator.  We call this collection of systems and technologies the Quantum Network Analyzer(QNA) in analog to the Vector Network Analyzer(VNA) terminology in widespread use in radio frequency measurements.  

The work shared here is a work in progress, and all components here are in a prototype phase at the time of this writing.(June 2024).

  - [3d printed parts](3dprint/)
  - [BUD box modifications](bud-box/)
  - [Rack Mount Front Panel Assembly](rack-mount-front-panel-assembly/)
  - [Arduino shield](pcb/arduino-to-headers-shield/)
  - [Arduino Code for SP9T Switch](Arduino-code/9-port-controller/9-port-controller.ino)
  - [DSUB and relay board](pcb/DB25-relay-HV-control/)
  - [Cold Mechanical Assembly](cold-mechanical/)
  - [Micro D breakout board](pcb/microd-header-adapter-board-rev2/)
  - [RF Switch Board](pcb/rectangle11/)
  - [RF calibration boards](pcb/calboards/)

## Rack Mount Control Panel

# 3d Printed parts

## Thread Inserts

(https://www.3djake.com/ruthex/threaded-insert-4-40-unc-100-pieces)

## 4-40 quarter inch screws

(https://www.mcmaster.com/90272A106/)

## Arduino Bracket

Use 4-40 brass thread inserts, press them in with a soldering iron

arduino-bracket.STL 

## DC DC converter Bracket

Use 4-40 brass thread inserts, press them in with a soldering iron

HV-DCDC-bracket.STL 

## Front Panel Edge Bracket

Use 4-40 brass thread inserts, press them in with a soldering iron. Attach to wood with #4 wood screws. 

front-panel-edge-bracket.STL 

## Front Panel Center Bracket

place in center area of circuit board to prevent bowing, use #4 wood screws to mount.

front-panel-center-bracket.STL 

## Circuit Boards for Rack Mount

# System Elements

 - rack mount controller
 	- wood panel
 	- button and light control board
 	- aluminum enclosure
 	- DB25 board
 	- arduino shield
 	- arduino code
 	- arduino UNO
 	- 3d printed parts
 	- DC DC converters
 - cold assembly
 	- h bracket
 	- standoff
 	- outside bracket
 	- center bracket
 	- hex standoffs
 	- rectangle 11 board
 	- microD breakout board

# Rack Mount Controller



## Wood Panel

Buy a 24 inch long by 4 inch wide 1/2 inch thick white oak board:

[](https://ocoochhardwoods.com/scroll-saw-lumber/WhiteOak/ 
)

[](https://ocoochhardwoods.com/scroll-saw-lumber/WhiteOak/ 
)

Cut it down to 19 inches, and sand off rough edges of saw cut.

Drill loose #10 clearance holes in from edges 5/16" in from edge and up and down from center by 1.5 inches.

## Bud box









## To do:

 - add dimensioned drawings to brackets in this document
 - add dimensioned drawing of Arduino UNO with all the holes
 - add all the Altium files and screen shots including schematics, and bills of materials
 - add all the gerber files with information about orders from pcbway
 - add links to all the data sheets
 - build a front panel for the 6 port switches using frontpanel express
 - write and test the code for the six port switch, get more information on that from Logan and Jordan
 - figure out how to add the dc connectors myself without getting those sent out
 - test every single pin
 - rewrite code for 8 port switch and test it
 - build an 8 port front panel 
 - look into larger wood screws or different heads so they don't strip as easily
 - add buttons, lights, resistors to this document
 - add capacitors to this document
 - add headers to this document
 - add arduino code to this document(6 pole, 9 pole, 8 pole)
 - add python control code to this document
 - add matlab control code to this document
 - add links to Hamdi's switches, links to Eval kit boards, description of the 8 poirt

# Front Panel Wood Board Assembly

## Board: 1/2 inch by 4 inches by 19 inches, cut from 24 inches

(https://ocoochhardwoods.com/detail/?i=124wo)

## Wood screws

## 5V to 12V boost

(https://www.amazon.com/Voltage-Converter-Vintage-Indicator-80V-380V/dp/B09D93QNYK/ref=pd_vtp_h_pd_vtp_h_d_sccl_3/135-2213394-8928934)

## 12 V to 90 V boost

(https://www.amazon.com/DROK-Boost-Converter-Regulator-Length/dp/B09M3LMSS3/)





```

#include <Adafruit_NeoPixel.h>
#ifdef __AVR__
#endif

// Which pin on the Arduino is connected to the NeoPixels?
#define PIN 19 // On Trinket or Gemma, suggest changing this to 1

// How many NeoPixels are attached to the Arduino?
#define NUMPIXELS 9 // 
//there are 9

// When setting up the NeoPixel library, we tell it how many pixels,  
// and which pin to use to send signals. Note that for older NeoPixel
// strips you might need to change the third parameter -- see the
// strandtest example for more information on possible values.
Adafruit_NeoPixel pixels(NUMPIXELS, PIN, NEO_GRB + NEO_KHZ800);

#define U4_123 2
#define U4_456 3
#define U4_789 4
#define U4_COM 5

#define U1_1 14
#define U1_2 15
#define U1_3 16
#define U1_COM 17

#define U2_4 10
#define U2_5 11
#define U2_6 12
#define U2_COM 13

#define U3_7 6
#define U3_8 7
#define U3_9 8
#define U3_COM 9

int analog = 0;
int delta = 20;
int mode = 1;//modes are 1,2,3,4,5,6,7,8,9 which are pixel 8,7,6,5,4,3,2,1, and 0 respectively

void setup() {
    Serial.begin(115200);

  // These lines are specifically to support the Adafruit Trinket 5V 16 MHz.
  // Any other board, you can remove this part (but no harm leaving it):
#if defined(__AVR_ATtiny85__) && (F_CPU == 16000000)
  clock_prescale_set(clock_div_1);
#endif
  // END of Trinket-specific code.

/*
    pinMode(2,OUTPUT);// DSUB 8,  U4 -> U1
    pinMode(3,OUTPUT);// DSUB 9,  U4 -> U2
    pinMode(4,OUTPUT);// DSUB 10, U4 -> U3
    pinMode(5,OUTPUT);// DSUB 11, U4 COM
    pinMode(6,OUTPUT);// DSUB 14, U3 -> port 7
    pinMode(7,OUTPUT);// DSUB 15, U3 -> port 8
    pinMode(8,OUTPUT);// DSUB 16, U3 -> port 9
    pinMode(9,OUTPUT);// DSUB 17, U3 COM
    pinMode(10,OUTPUT);//DSUB 18, U2 -> 4 
    pinMode(11,OUTPUT);//DSUB 19, U2 -> 5
    pinMode(12,OUTPUT);//DSUB 20, U2 -> 6
    pinMode(13,OUTPUT);//DSUB 21, U2 COM
    pinMode(14,OUTPUT);//DSUB 22, U1 -> 1
    pinMode(15,OUTPUT);//DSUB 23, U1 -> 2
    pinMode(16,OUTPUT);//DSUB 24, U1 -> 3
    pinMode(17,OUTPUT);//DSUB 25, U1 COM
*/

    pinMode(U4_COM,OUTPUT);
    pinMode(U4_123,OUTPUT);
    pinMode(U4_456,OUTPUT);
    pinMode(U4_789,OUTPUT);

    pinMode(U1_COM,OUTPUT);
    pinMode(U1_1,OUTPUT);
    pinMode(U1_2,OUTPUT);
    pinMode(U1_3,OUTPUT);

    pinMode(U2_COM,OUTPUT);
    pinMode(U2_4,OUTPUT);
    pinMode(U2_5,OUTPUT);
    pinMode(U2_6,OUTPUT);

    pinMode(U3_COM,OUTPUT);
    pinMode(U3_7,OUTPUT);
    pinMode(U3_8,OUTPUT);
    pinMode(U3_9,OUTPUT);

    digitalWrite(U1_COM,HIGH);
    digitalWrite(U2_COM,HIGH);
    digitalWrite(U3_COM,HIGH);
    digitalWrite(U4_COM,HIGH);

    digitalWrite(U4_123,HIGH);
    digitalWrite(U4_456,LOW);
    digitalWrite(U4_789,LOW);

    digitalWrite(U1_1,HIGH);
    digitalWrite(U1_2,LOW);
    digitalWrite(U1_3,LOW);
 
    digitalWrite(U2_4,LOW);
    digitalWrite(U2_5,LOW);
    digitalWrite(U2_6,LOW);

    digitalWrite(U3_7,LOW);
    digitalWrite(U3_8,LOW);
    digitalWrite(U3_9,LOW);

  pixels.begin(); // INITIALIZE NeoPixel strip object (REQUIRED)

}

void loop() {

  pixels.clear(); // Set all pixel colors to 'off'
  analog = analogRead(A4);
  // The first NeoPixel in a strand is #0, second is 1, all the way up
  // to the count of pixels minus one.
  
  if(analog > 1024 - delta){
    delay(1);
    analog = analogRead(A4);
    if(analog > 1023 - delta){
       mode = 1;      
    }
  }
  if(analog > 836 - delta && analog < 836 + delta){
    delay(5);
    analog = analogRead(A4);
    if(analog > 836 - delta && analog < 836 + delta){
         mode = 2; 
    }
  }
  if(analog > 690 - delta && analog < 690 + delta){
     delay(5);
     analog = analogRead(A4);

    if(analog > 690 - delta && analog < 690 + delta){
      mode = 3;    
    }
  }

  if(analog > 569 - delta && analog < 569 + delta){
     delay(1);
     analog = analogRead(A4);

    if(analog > 569 - delta && analog < 569 + delta){
      mode = 4;    
    }
  }

  if(analog > 464 - delta && analog < 464 + delta){
     delay(1);
     analog = analogRead(A4);

    if(analog > 464 - delta && analog < 464 + delta){
      mode = 5;    
    }
  }

  if(analog > 372 - delta && analog < 372 + delta){
     delay(1);
     analog = analogRead(A4);

    if(analog > 372 - delta && analog < 372 + delta){
      mode = 6;    
    }
  }

  if(analog > 283 - delta && analog < 283 + delta){
     delay(1);
     analog = analogRead(A4);

    if(analog > 283 - delta && analog < 283 + delta){
      mode = 7;    
    }
  }

  if(analog > 195 - delta && analog < 195 + delta){
     delay(1);
     analog = analogRead(A4);

    if(analog > 195 - delta && analog < 195 + delta){
      mode = 8;    
    }
  }

  if(analog > 103 - delta && analog < 103 + delta){
     delay(1);
     analog = analogRead(A4);

    if(analog > 103 - delta && analog < 103 + delta){
      mode = 9;    
    }
  }

  if (Serial.available()) {

    //for more info on this code see http://adam-meyer.com/arduino/arduino-serial
    //read serial as ascii integer
     int ser = Serial.read();
    //    Serial.println(ser);
     if(ser == 49){    //ASCII for 1
      mode = 1;
     }
     if(ser == 50){    //ASCII for 2
      mode = 2;
     }
     if(ser == 51){    //ASCII for 3
      mode = 3;
     }
     if(ser == 52){    //ASCII for 4
      mode = 4;
     }
     if(ser == 53){    //ASCII for 5
      mode = 5;
     }
     if(ser == 54){    //ASCII for 6
      mode = 6;
     }
     if(ser == 55){    //ASCII for 4
      mode = 7;
     }
     if(ser == 56){    //ASCII for 5
      mode = 8;
     }
     if(ser == 57){    //ASCII for 6
      mode = 9;
     }

  }

  if(mode == 1){
    pixels.setPixelColor(0, pixels.Color(0, 0, 0));    
    pixels.setPixelColor(1, pixels.Color(0, 0, 0));    
    pixels.setPixelColor(2, pixels.Color(0, 0, 0));    
    pixels.setPixelColor(3, pixels.Color(0, 0, 0));    
    pixels.setPixelColor(4, pixels.Color(0, 0, 0));    
    pixels.setPixelColor(5, pixels.Color(0, 0, 0));    
    pixels.setPixelColor(6, pixels.Color(0, 0, 0));    
    pixels.setPixelColor(7, pixels.Color(0, 0, 0));    
    pixels.setPixelColor(8, pixels.Color(255, 0, 0));    

    digitalWrite(U4_123,HIGH);
    digitalWrite(U4_456,LOW);
    digitalWrite(U4_789,LOW);

    digitalWrite(U1_1,HIGH);
    digitalWrite(U1_2,LOW);
    digitalWrite(U1_3,LOW);
 
    digitalWrite(U2_4,LOW);
    digitalWrite(U2_5,LOW);
    digitalWrite(U2_6,LOW);

    digitalWrite(U3_7,LOW);
    digitalWrite(U3_8,LOW);
    digitalWrite(U3_9,LOW);

  }
  if(mode == 2){
    pixels.setPixelColor(0, pixels.Color(0, 0, 0));    
    pixels.setPixelColor(1, pixels.Color(0, 0, 0));    
    pixels.setPixelColor(2, pixels.Color(0, 0, 0));    
    pixels.setPixelColor(3, pixels.Color(0, 0, 0));    
    pixels.setPixelColor(4, pixels.Color(0, 0, 0));    
    pixels.setPixelColor(5, pixels.Color(0, 0, 0));    
    pixels.setPixelColor(6, pixels.Color(0, 0, 0));    
    pixels.setPixelColor(7, pixels.Color(255, 0, 0));    
    pixels.setPixelColor(8, pixels.Color(0, 0, 0));    
    
    digitalWrite(U4_123,HIGH);
    digitalWrite(U4_456,LOW);
    digitalWrite(U4_789,LOW);

    digitalWrite(U1_1,LOW);
    digitalWrite(U1_2,HIGH);
    digitalWrite(U1_3,LOW);
 
    digitalWrite(U2_4,LOW);
    digitalWrite(U2_5,LOW);
    digitalWrite(U2_6,LOW);

    digitalWrite(U3_7,LOW);
    digitalWrite(U3_8,LOW);
    digitalWrite(U3_9,LOW);
 
  }
  if(mode == 3){
    pixels.setPixelColor(0, pixels.Color(0, 0, 0));    
    pixels.setPixelColor(1, pixels.Color(0, 0, 0));    
    pixels.setPixelColor(2, pixels.Color(0, 0, 0));    
    pixels.setPixelColor(3, pixels.Color(0, 0, 0));    
    pixels.setPixelColor(4, pixels.Color(0, 0, 0));    
    pixels.setPixelColor(5, pixels.Color(0, 0, 0));    
    pixels.setPixelColor(6, pixels.Color(255, 0, 0));    
    pixels.setPixelColor(7, pixels.Color(0, 0, 0));    
    pixels.setPixelColor(8, pixels.Color(0, 0, 0));    
    
    digitalWrite(U4_123,HIGH);
    digitalWrite(U4_456,LOW);
    digitalWrite(U4_789,LOW);

    digitalWrite(U1_1,LOW);
    digitalWrite(U1_2,LOW);
    digitalWrite(U1_3,HIGH);
 
    digitalWrite(U2_4,LOW);
    digitalWrite(U2_5,LOW);
    digitalWrite(U2_6,LOW);

    digitalWrite(U3_7,LOW);
    digitalWrite(U3_8,LOW);
    digitalWrite(U3_9,LOW);    

  }
  if(mode == 4){
    pixels.setPixelColor(0, pixels.Color(0, 0, 0));    
    pixels.setPixelColor(1, pixels.Color(0, 0, 0));    
    pixels.setPixelColor(2, pixels.Color(0, 0, 0));    
    pixels.setPixelColor(3, pixels.Color(0, 0, 0));    
    pixels.setPixelColor(4, pixels.Color(0, 0, 0));    
    pixels.setPixelColor(5, pixels.Color(255, 0, 0));    
    pixels.setPixelColor(6, pixels.Color(0, 0, 0));    
    pixels.setPixelColor(7, pixels.Color(0, 0, 0));    
    pixels.setPixelColor(8, pixels.Color(0, 0, 0));    
    
    digitalWrite(U4_123,LOW);
    digitalWrite(U4_456,HIGH);
    digitalWrite(U4_789,LOW);

    digitalWrite(U1_1,LOW);
    digitalWrite(U1_2,LOW);
    digitalWrite(U1_3,LOW);
 
    digitalWrite(U2_4,HIGH);
    digitalWrite(U2_5,LOW);
    digitalWrite(U2_6,LOW);

    digitalWrite(U3_7,LOW);
    digitalWrite(U3_8,LOW);
    digitalWrite(U3_9,LOW);    

  }
  if(mode == 5){
    pixels.setPixelColor(0, pixels.Color(0, 0, 0));    
    pixels.setPixelColor(1, pixels.Color(0, 0, 0));    
    pixels.setPixelColor(2, pixels.Color(0, 0, 0));    
    pixels.setPixelColor(3, pixels.Color(0, 0, 0));    
    pixels.setPixelColor(4, pixels.Color(255, 0, 0));    
    pixels.setPixelColor(5, pixels.Color(0, 0, 0));    
    pixels.setPixelColor(6, pixels.Color(0, 0, 0));    
    pixels.setPixelColor(7, pixels.Color(0, 0, 0));    
    pixels.setPixelColor(8, pixels.Color(0, 0, 0));    

    digitalWrite(U4_123,LOW);
    digitalWrite(U4_456,HIGH);
    digitalWrite(U4_789,LOW);

    digitalWrite(U1_1,LOW);
    digitalWrite(U1_2,LOW);
    digitalWrite(U1_3,LOW);
 
    digitalWrite(U2_4,LOW);
    digitalWrite(U2_5,HIGH);
    digitalWrite(U2_6,LOW);

    digitalWrite(U3_7,LOW);
    digitalWrite(U3_8,LOW);
    digitalWrite(U3_9,LOW);    

  }
  if(mode == 6){
    pixels.setPixelColor(0, pixels.Color(0, 0, 0));    
    pixels.setPixelColor(1, pixels.Color(0, 0, 0));    
    pixels.setPixelColor(2, pixels.Color(0, 0, 0));    
    pixels.setPixelColor(3, pixels.Color(255, 0, 0));    
    pixels.setPixelColor(4, pixels.Color(0, 0, 0));    
    pixels.setPixelColor(5, pixels.Color(0, 0, 0));    
    pixels.setPixelColor(6, pixels.Color(0, 0, 0));    
    pixels.setPixelColor(7, pixels.Color(0, 0, 0));    
    pixels.setPixelColor(8, pixels.Color(0, 0, 0));    

    digitalWrite(U4_123,LOW);
    digitalWrite(U4_456,HIGH);
    digitalWrite(U4_789,LOW);

    digitalWrite(U1_1,LOW);
    digitalWrite(U1_2,LOW);
    digitalWrite(U1_3,LOW);
 
    digitalWrite(U2_4,LOW);
    digitalWrite(U2_5,LOW);
    digitalWrite(U2_6,HIGH);

    digitalWrite(U3_7,LOW);
    digitalWrite(U3_8,LOW);
    digitalWrite(U3_9,LOW);

  }

  if(mode == 7){
    pixels.setPixelColor(0, pixels.Color(0, 0, 0));    
    pixels.setPixelColor(1, pixels.Color(0, 0, 0));    
    pixels.setPixelColor(2, pixels.Color(255, 0, 0));    
    pixels.setPixelColor(3, pixels.Color(0, 0, 0));    
    pixels.setPixelColor(4, pixels.Color(0, 0, 0));    
    pixels.setPixelColor(5, pixels.Color(0, 0, 0));    
    pixels.setPixelColor(6, pixels.Color(0, 0, 0));    
    pixels.setPixelColor(7, pixels.Color(0, 0, 0));    
    pixels.setPixelColor(8, pixels.Color(0, 0, 0));    

    digitalWrite(U4_123,LOW);
    digitalWrite(U4_456,LOW);
    digitalWrite(U4_789,HIGH);

    digitalWrite(U1_1,LOW);
    digitalWrite(U1_2,LOW);
    digitalWrite(U1_3,LOW);
 
    digitalWrite(U2_4,LOW);
    digitalWrite(U2_5,LOW);
    digitalWrite(U2_6,LOW);

    digitalWrite(U3_7,HIGH);
    digitalWrite(U3_8,LOW);
    digitalWrite(U3_9,LOW);

 }
  if(mode == 8){
    pixels.setPixelColor(0, pixels.Color(0, 0, 0));    
    pixels.setPixelColor(1, pixels.Color(255, 0, 0));    
    pixels.setPixelColor(2, pixels.Color(0, 0, 0));    
    pixels.setPixelColor(3, pixels.Color(0, 0, 0));    
    pixels.setPixelColor(4, pixels.Color(0, 0, 0));    
    pixels.setPixelColor(5, pixels.Color(0, 0, 0));    
    pixels.setPixelColor(6, pixels.Color(0, 0, 0));    
    pixels.setPixelColor(7, pixels.Color(0, 0, 0));    
    pixels.setPixelColor(8, pixels.Color(0, 0, 0));    

    digitalWrite(U4_123,LOW);
    digitalWrite(U4_456,LOW);
    digitalWrite(U4_789,HIGH);

    digitalWrite(U1_1,LOW);
    digitalWrite(U1_2,LOW);
    digitalWrite(U1_3,LOW);
 
    digitalWrite(U2_4,LOW);
    digitalWrite(U2_5,LOW);
    digitalWrite(U2_6,LOW);

    digitalWrite(U3_7,LOW);
    digitalWrite(U3_8,HIGH);
    digitalWrite(U3_9,LOW);

  }
  if(mode == 9){
    pixels.setPixelColor(0, pixels.Color(255, 0, 0));    
    pixels.setPixelColor(1, pixels.Color(0, 0, 0));    
    pixels.setPixelColor(2, pixels.Color(0, 0, 0));    
    pixels.setPixelColor(3, pixels.Color(0, 0, 0));    
    pixels.setPixelColor(4, pixels.Color(0, 0, 0));    
    pixels.setPixelColor(5, pixels.Color(0, 0, 0));    
    pixels.setPixelColor(6, pixels.Color(0, 0, 0));    
    pixels.setPixelColor(7, pixels.Color(0, 0, 0));    
    pixels.setPixelColor(8, pixels.Color(0, 0, 0));    

    digitalWrite(U4_123,LOW);
    digitalWrite(U4_456,LOW);
    digitalWrite(U4_789,HIGH);

    digitalWrite(U1_1,LOW);
    digitalWrite(U1_2,LOW);
    digitalWrite(U1_3,LOW);
 
    digitalWrite(U2_4,LOW);
    digitalWrite(U2_5,LOW);
    digitalWrite(U2_6,LOW);

    digitalWrite(U3_7,LOW);
    digitalWrite(U3_8,LOW);
    digitalWrite(U3_9,HIGH);

  }

  pixels.show();   // Send the updated pixel colors to the hardware.
  delay(1); // Pause before next pass through loop

//    Serial.println(analog);

}

```

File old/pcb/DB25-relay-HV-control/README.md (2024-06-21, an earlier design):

## [Up to PCB/](../)



 
 
# DB25-relay-HV-control Printed Circuit Board(PCB)





## Bill of Materials



 - [PCB's](https://www.pcbway.com)
 - [1 MOhm 1206 SMT resistors]()
 - [DB25 board mount connector]()
 - [relays]()
 - [header strips (40 pins)](https://www.digikey.com/en/products/detail/amphenol-cs-commercial-products/G800W268018EU/17083164)

## Files

 - [Altium Schematic .SchDoc](DB25-relay-HV-control.schDoc)
 - [Altium project file .PrjPcb](DB25-relay-HV-control.PrjPcb)
 - [Altium Pcb File .PcbDoc](DB25-relay-HV-control.PrjPcb)
 - [.zip of Gerber files](DB25-relay-HV-control-gerbers.zip)

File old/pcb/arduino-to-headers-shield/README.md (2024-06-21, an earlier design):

## [Up to PCB/](../)





# arduino-to-headers-shield Printed Circuit Board(PCB)



## Bill of Materials



 - [PCB's](https://www.pcbway.com)
 - [330 ohm resistors]()
 - [100k resistors]()
 - [1000 uF Capacitors]()
 - [header strips (40 pins)](https://www.digikey.com/en/products/detail/amphenol-cs-commercial-products/G800W268018EU/17083164)

[Digkey Cart with everything but PCB's](https://www.digikey.com/short/jzc9cpp0)

## Files

 - [Altium Schematic .SchDoc](arduino-to-headers-shield.schDoc)
 - [Altium project file .PrjPcb](arduino-to-headers-shield.PrjPcb)
 - [Altium Pcb File .PcbDoc](arduino-to-headers-shield.PrjPcb)
 - [.zip of Gerber files](arduino-to-headers-shield-gerbers.zip)

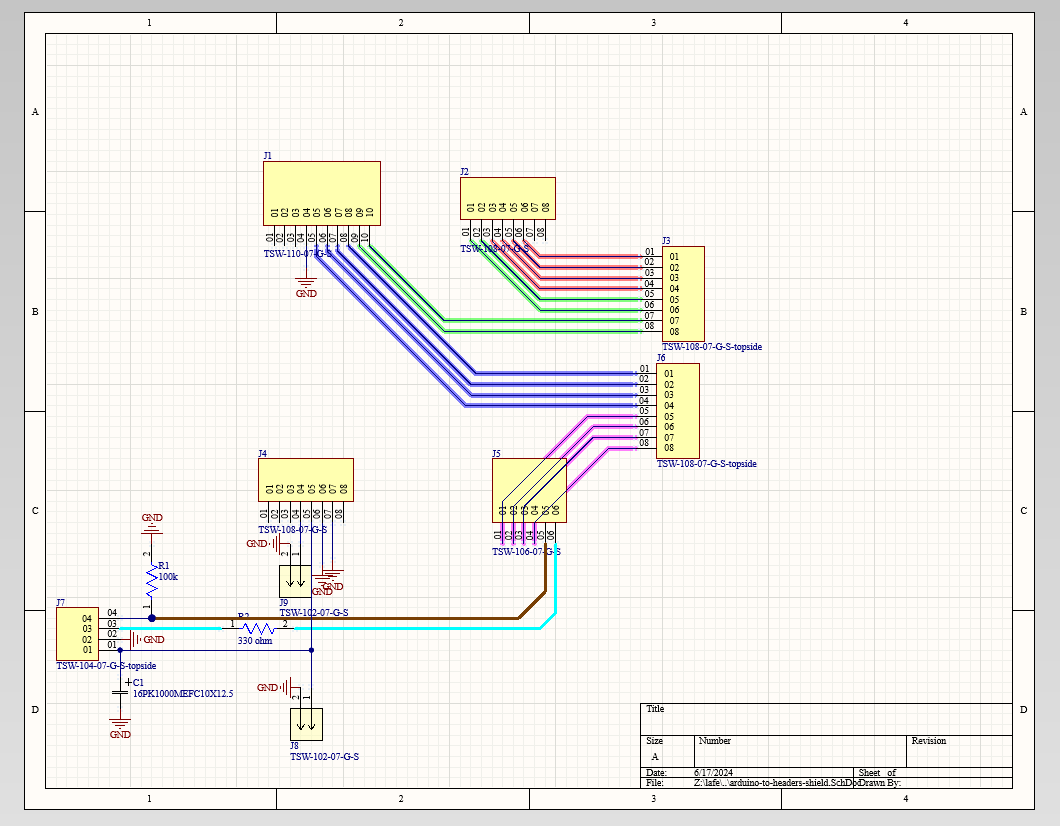
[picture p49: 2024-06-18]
pcb/arduino-to-headers-shield/images/arduino-to-headers-shield-altium-schematic-screenshot.png

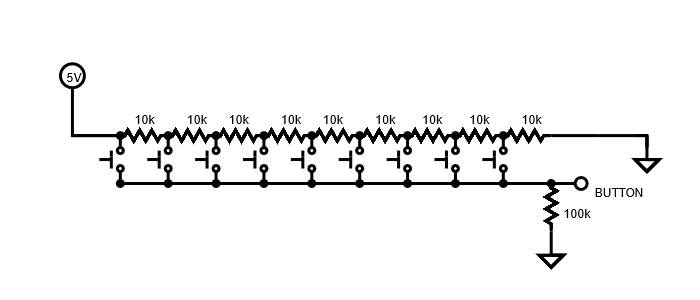
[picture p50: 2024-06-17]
pcb/9button-9neopixels/images/buttons-schematic.png

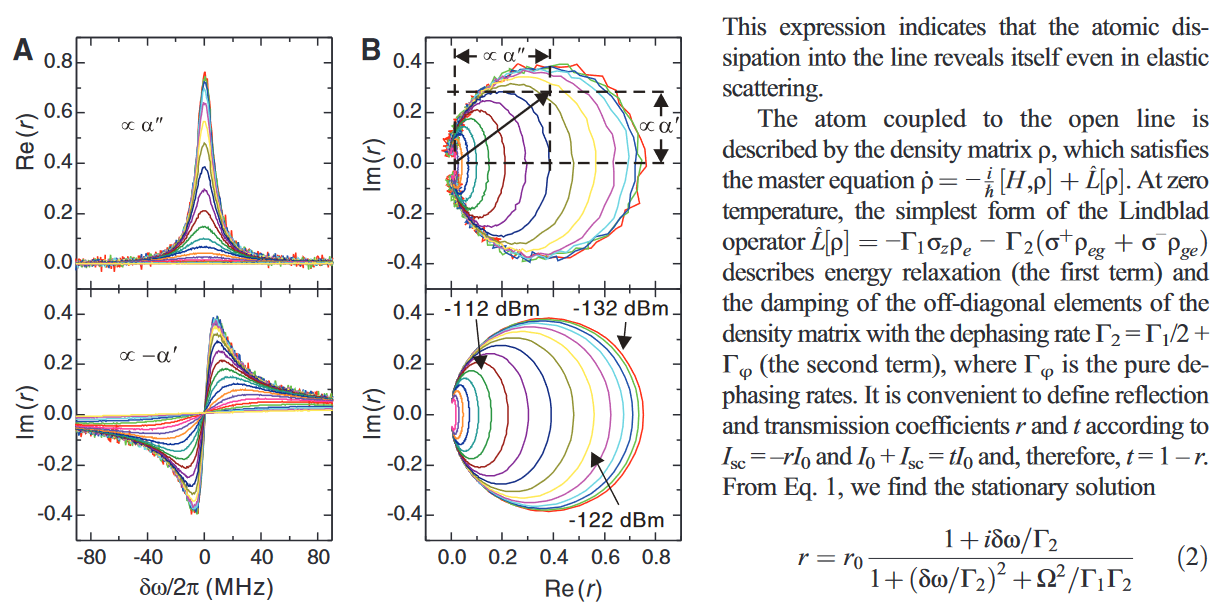
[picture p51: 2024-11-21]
images/nakamura-artificial-atom-science-paper-screenshot.png

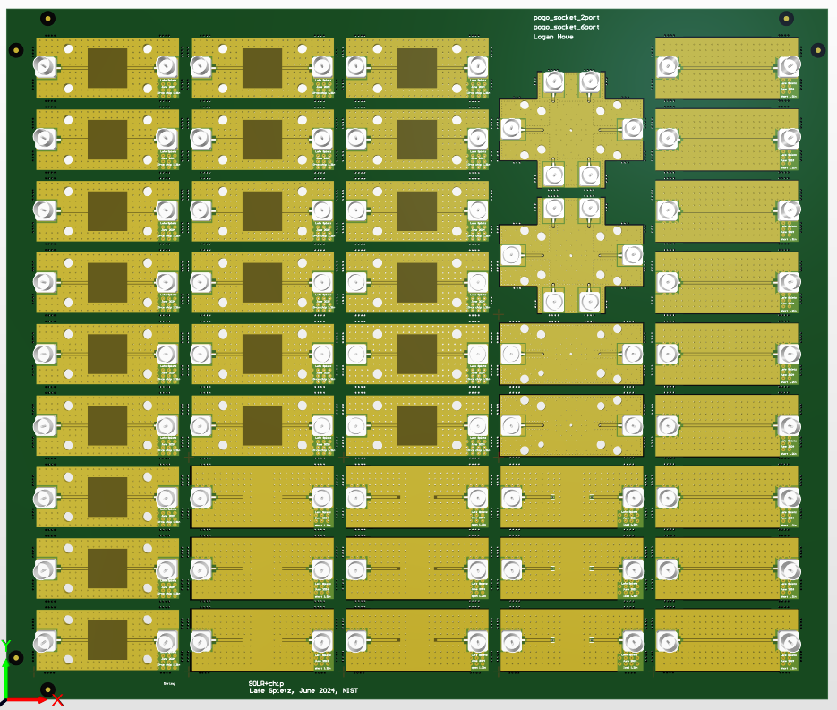
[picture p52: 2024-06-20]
images/cal-boards-panelization1.PNG

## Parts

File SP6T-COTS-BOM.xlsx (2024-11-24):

description | link to buy | unit price | number | extended price | vendor | vendor part number | manfacturer | manufacturer part number
1/2" White oak board, 4" x 24" | https://ocoochhardwoods.com/detail/?i=124wo | $5.40 | 1 | $5.40 | Ocooch Hardwoods |  | Ocooch Hardwoods
Brass Flared-Collar Knurled-Head Thumb Screws 10-32 Thread Size, 3/4" Long | https://www.mcmaster.com/92421A645/ | $1.62 | 4 | $6.48 | McMaster Carr | 92421A645
#6 wood screws | https://www.amazon.com/Stainless-Phillips-Screws-Multipurpose-TPOHH/dp/B0CHRWGT8N | $0.07 | 8 | $0.56 | Amazon
cryoelec-bracket | https://github.com/lafefspietz/MEMSduino/raw/refs/heads/main/cryoelec-bracket.STL |  | 1 |  | in house prototype
arduino-bracket | https://github.com/lafefspietz/MEMSduino/raw/refs/heads/main/arduino-bracket.STL |  | 1 |  | in house prototype
front-panel-edge-bracket | https://github.com/lafefspietz/MEMSduino/raw/refs/heads/main/front-panel-edge-bracket.STL |  | 2 |  | in house prototype
Brass threaded inserts #4-40 | https://www.3djake.com/ruthex/threaded-insert-4-40-unc-100-pieces | $0.08 | 7 | $0.57 | 3dJake | RUT-GE-4-40x57-001 | ruthex | GE-4-40x57-001
0-80 Brass Thread Inserts(E-Z LOK 240-000-BR) | https://www.amazon.com/Z-LOK-Threaded-Insert-Plastic/dp/B08QJJDCW1/ | $0.47 | 4 | $1.88 | Amazon | B08QJJDCW1 | E-Z LOK | 240-000-BR
Zinc-Plated Steel Pan Head Phillips Screw 4-40 Thread, 1/4" Long | https://www.mcmaster.com/90272A106/ | $0.02 | 9 | $0.16 | McMaster Carr | 90272A106
Diecast aluminum enclosure, AN-1304-A from BUD Industries | https://www.digikey.com/en/products/detail/bud-industries/AN-1304-A/5804538 | $14.90 | 1 | $14.90 | Digikey | 377-2395-ND | Bud Industries | AN-1304-A
Male-Female Threaded Hex Standoff 18-8 Stainless Steel, 3/16" Hex, 7/32" Long, 4-40 to 4-40 Thread | https://www.mcmaster.com/91075A462/ | $3.73 | 2 | $7.46 | McMaster Carr | 91075A462
Brass Socket Head Screw 4-40 Thread Size, 3/4" Long | https://www.mcmaster.com/93465A113/ | $1.20 | 2 | $2.40 | McMaster Carr | 93465A113
Brass Washer for Number 4 Screw Size, 0.12" ID, 0.281" OD | https://www.mcmaster.com/92916A320/ | $0.05 | 2 | $0.10 | McMaster Carr | 92916A320
6button-6neopixel, 152.4 mm x 88.9 mm (6"x3.5") | https://github.com/lafefspietz/MEMSduino/raw/refs/heads/main/6button-6neopixel-gerbers.zip | $5.98 | 1 | $5.98 | PCBWay
arduino-to-headers-shield 53.34 mm x 70.78 mm (2.1" x 2.79") | https://github.com/lafefspietz/MEMSduino/raw/refs/heads/main/arduino-to-headers-shield-gerbers.zip | $1.82 | 1 | $1.82 | PCBWay
100k axial resistor | https://www.digikey.com/en/products/detail/stackpole-electronics-inc/RNF14FTD100K/1706591 | $0.10 | 1 | $0.10 | Digikey | RNF14FTD100KCT-ND | Stackpole Electronics Inc | RNF14FTD100K
10k axial resistor | https://www.digikey.com/en/products/detail/yageo/MFR-25FBF52-10K/13219 | $0.05 | 9 | $0.45 | Digikey | 10.0KXBK-ND | YAGEO | MFR-25FBF52-10K
330 ohm axial resistor | https://www.digikey.com/en/products/detail/stackpole-electronics-inc/CF18JT330R/1741683 | $0.10 | 2 | $0.20 | Digikey | CF18JT330RCT-ND | Stackpole Electronics Inc | CF18JT330R
1000 uF electrolytic capacitor | https://www.digikey.com/en/products/detail/rubycon/16PK1000MEFC10X12-5/3563556 | $0.51 | 1 | $0.51 | Digikey | 1189-1719-ND | Rubycon | 16PK1000MEFC10X12.5
Momentary buttons | https://www.digikey.com/en/products/detail/e-switch/TL59NF160Q/390533 | $0.29 | 6 | $1.74 | Digikey | EG2532TB-ND | E Switch | TL59NF160Q
JUMPER WIRE M/M 6" 20PCS | https://www.digikey.com/en/products/detail/sparkfun-electronics/PRT-12795/5993860 | $2.10 | 1 | $2.10 | Digikey | 1568-1512-ND | Sparkfun | PRT-12795
DB25 panel mount solder cup | https://www.digikey.com/en/products/detail/norcomp-inc/171-025-103L001/858135 | $2.16 | 1 | $2.16 | Digikey | 225ME-ND | NorComp Inc. | 171-025-103L001
Arduino UNO | https://www.digikey.com/en/products/detail/dfrobot/DFR0216/6579366 | $16.90 | 1 | $16.90 | Digikey | 1738-1228-ND | DFRobot | DFR0216
USB A to USB B cable | https://www.digikey.com/en/products/detail/assmann-wsw-components/AK672-2-2/947492 | $1.64 | 1 | $1.64 | Digikey | AE1493-ND | Assmann WSW Components | AK672/2-2
Neopixel programmable RGB LED | https://www.adafruit.com/product/1559 | $1.25 | 6 | $7.50 | Adafruit | 1559 | Adafruit | 1559
2 wire header cable | https://www.amazon.com/ZYAMY-Dupont-Connector-Multicolor-Breadboard/dp/B0B8Z23NWX/ | $0.60 | 1 | $0.60 | Amazon
4 wire header cable | https://www.amazon.com/ZYAMY-Dupont-Connector-Multicolor-Breadboard/dp/B0789F523N/ | $0.79 | 9 | $7.11 | Amazon
8 wire header cable | https://www.amazon.com/ZYAMY-Dupont-Connector-Multicolor-Breadboard/dp/B0789F2Y1T/ | $0.99 | 2 | $1.98 | Amazon
0.1" headers | https://www.amazon.com/Header-Lystaii-Pin-Connector-Electronic/dp/B06ZZN8L9S/ | $0.09 | 3 | $0.27 | Amazon
DB25 to Fischer Cable | https://aivon.fi |  | 1 |  | Aivon
 |  |  |  | $61.02

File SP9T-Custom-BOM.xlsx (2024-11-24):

description | link | unit price | number | extended price | vendor | vendor part number | manfacturer | manufacturer part number
1/2" White oak board, 4" x 24" | https://ocoochhardwoods.com/detail/?i=124wo | $5.40 | 1 | $5.40 | Ocooch Hardwoods |  | Ocooch Hardwoods
Brass Flared-Collar Knurled-Head Thumb Screws 10-32 Thread Size, 3/4" Long | https://www.mcmaster.com/92421A645/ | $1.62 | 4 | $6.48 | McMaster Carr | 92421A645
#6 wood screws | https://www.amazon.com/Stainless-Phillips-Screws-Multipurpose-TPOHH/dp/B0CHRWGT8N | $0.07 | 10 | $0.70 | Amazon
HV-DCDC-bracket.STL 3d print(4 g of filament, 14 minutes print time) | https://github.com/lafefspietz/MEMSduino/raw/refs/heads/main/HV-DCDC-bracket.STL |  | 1 |  | in house prototype
arduino-bracket.STL 3d print(4 g of filament, 17 minutes print time) | https://github.com/lafefspietz/MEMSduino/raw/refs/heads/main/arduino-bracket.STL |  | 1 |  | in house prototype
front-panel-edge-bracket.STL 3d print (3 g of filament, 14 minutes print time) | https://github.com/lafefspietz/MEMSduino/raw/refs/heads/main/front-panel-edge-bracket.STL |  | 2 |  | in house prototype
front-panel-center-bracket 3d print (1 g of filament, 7 minutes print time) | https://github.com/lafefspietz/MEMSduino/raw/refs/heads/main/front-panel-center-bracket.STL |  | 2 |  | in house prototype
Brass threaded inserts #4-40 | https://www.3djake.com/ruthex/threaded-insert-4-40-unc-100-pieces | $0.08 | 11 | $0.89 | 3dJake | RUT-GE-4-40x57-001 | ruthex | GE-4-40x57-001
Zinc-Plated Steel Pan Head Phillips Screw 4-40 Thread, 1/4" Long | https://www.mcmaster.com/90272A106/ | $0.02 | 11 | $0.20 | McMaster Carr | 90272A106
Diecast aluminum enclosure, AN-1304-A from BUD Industries | https://www.digikey.com/en/products/detail/bud-industries/AN-1304-A/5804538 | $14.90 | 1 | $14.90 | Digikey | 377-2395-ND | Bud Industries | AN-1304-A
Male-Female Threaded Hex Standoff 18-8 Stainless Steel, 3/16" Hex, 7/32" Long, 4-40 to 4-40 Thread | https://www.mcmaster.com/91075A462/ | $3.73 | 2 | $7.46 | McMaster Carr | 91075A462
Brass Socket Head Screw 4-40 Thread Size, 3/4" Long | https://www.mcmaster.com/93465A113/ | $1.20 | 2 | $2.40 | McMaster Carr | 93465A113
Brass Washer for Number 4 Screw Size, 0.12" ID, 0.281" OD | https://www.mcmaster.com/92916A320/ | $0.05 | 2 | $0.10 | McMaster Carr | 92916A320
5V-12V boost | https://www.amazon.com/KUNCAN-Converter-Cable-Voltage-Connector/dp/B01ID90K4A/?th=1 | $11.99 | 1 | $11.99 | Amazon | B01ID90K4A | KUNCAN | KC-SU-10-2
12V to HV boost | https://www.amazon.com/Voltage-Converter-Vintage-Indicator-80V-380V/dp/B09D93QNYK | $11.39 | 1 | $11.39 | Amazon | B09D93QNYK | QINIZX | NIXIE-HV380V
heat shrink tubing | https://www.digikey.com/en/products/detail/3m/SFTW203-1-16-BL-SPL/22044171 | $1.89 | 1 | $1.89 | Digikey | 19-SFTW2031/16"BLSPL-DS-ND | 3M | SFTW203 1/16" BL SPL
9button-9neopixel 228.6mm x 88.9mm (9" x 3.5") printed circuit board | https://github.com/lafefspietz/MEMSduino/raw/refs/heads/main/9button-9neopixel-gerbers.zip | $5.98 | 1 | $5.98 | PCBWay
arduino-to-headers-shield 53.34 mm x 70.78 mm (2.1" x 2.79") printed circuit board | https://github.com/lafefspietz/MEMSduino/raw/refs/heads/main/arduino-to-headers-shield-gerbers.zip | $1.82 | 1 | $1.82 | PCBWay
DB25-relay-HV-control 78.74 mm x 71.12 mm (3.1"x2.8") printed circuit board | https://github.com/lafefspietz/MEMSduino/raw/refs/heads/main/DB25-relay-HV-control-gerbers.zip | $1.82 | 1 | $1.82 | PCBWay
100k axial resistor | https://www.digikey.com/en/products/detail/stackpole-electronics-inc/RNF14FTD100K/1706591 | $0.10 | 1 | $0.10 | Digikey | RNF14FTD100KCT-ND | Stackpole Electronics Inc | RNF14FTD100K
10k axial resistor | https://www.digikey.com/en/products/detail/yageo/MFR-25FBF52-10K/13219 | $0.05 | 9 | $0.45 | Digikey | 10.0KXBK-ND | YAGEO | MFR-25FBF52-10K
330 ohm axial resistor | https://www.digikey.com/en/products/detail/stackpole-electronics-inc/CF18JT330R/1741683 | $0.10 | 2 | $0.20 | Digikey | CF18JT330RCT-ND | Stackpole Electronics Inc | CF18JT330R
1000 uF electrolytic capacitor | https://www.digikey.com/en/products/detail/rubycon/16PK1000MEFC10X12-5/3563556 | $0.51 | 1 | $0.51 | Digikey | 1189-1719-ND | Rubycon | 16PK1000MEFC10X12.5
Momentary buttons | https://www.digikey.com/en/products/detail/e-switch/TL59NF160Q/390533 | $0.29 | 9 | $2.61 | Digikey | EG2532TB-ND | E Switch | TL59NF160Q
1 Mohm 1206 SMT resistor 1% | https://www.digikey.com/en/products/detail/yageo/RC1206FR-071ML/728388 | $0.02 | 20 | $0.40 | Digikey | 311-1.00MFRCT-ND | YAGEO | RC1206FR-071ML
DB25 board mount connector | https://www.digikey.com/en/products/detail/assmann-wsw-components/A-DF-25-PP-Z/1241794 | $1.17 | 1 | $1.17 | Digikey | AE10940-ND | Assmann WSW Components | A-DF 25 PP/Z
RELAY REED SIP SPST .5A 5V W/DIO | https://www.digikey.com/en/products/detail/comus-international/3570-1331-053/7497099 | $1.42 | 20 | $28.40 | Digikey | 1835-1117-ND | Comus International | 3570-1331-053
Arduino UNO | https://www.digikey.com/en/products/detail/dfrobot/DFR0216/6579366 | $16.90 | 1 | $16.90 | Digikey | 1738-1228-ND | DFRobot | DFR0216
USB A to USB B cable | https://www.digikey.com/en/products/detail/assmann-wsw-components/AK672-2-2/947492 | $1.64 | 1 | $1.64 | Digikey | AE1493-ND | Assmann WSW Components | AK672/2-2
Neopixel programmable RGB LED | https://www.adafruit.com/product/1559 | $1.25 | 9 | $11.25 | Adafruit | 1559 | Adafruit | 1559
2 wire header cable | https://www.amazon.com/ZYAMY-Dupont-Connector-Multicolor-Breadboard/dp/B0B8Z23NWX/ | $0.60 | 1 | $0.60 | Amazon
4 wire header cable | https://www.amazon.com/ZYAMY-Dupont-Connector-Multicolor-Breadboard/dp/B0789F523N/ | $0.79 | 9 | $7.11 | Amazon
8 wire header cable | https://www.amazon.com/ZYAMY-Dupont-Connector-Multicolor-Breadboard/dp/B0789F2Y1T/ | $0.99 | 2 | $1.98 | Amazon
0.1" headers | https://www.amazon.com/Header-Lystaii-Pin-Connector-Electronic/dp/B06ZZN8L9S/ | $0.09 | 3 | $0.27 | Amazon
 |  |  |  | $118.44

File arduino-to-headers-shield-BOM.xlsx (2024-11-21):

description | link to buy | unit price | number | extended price | vendor | vendor part number | manfacturer | manufacturer part number
100k axial resistor | https://www.digikey.com/en/products/detail/stackpole-electronics-inc/RNF14FTD100K/1706591 | $0.10 | 1 | $0.10 | Digikey | RNF14FTD100KCT-ND | Stackpole Electronics | RNF14FTD100K
330 ohm axial resistor | https://www.digikey.com/en/products/detail/stackpole-electronics-inc/CF18JT330R/1741683 | $0.10 | 1 | $0.10 | Digikey | CF18JT330RCT-ND | Stackpole Electronics | CF18JT330R
1000 uF electrolytic capacitor | https://www.digikey.com/en/products/detail/rubycon/16PK1000MEFC10X12-5/3563556 | $0.51 | 1 | $0.51 | Digikey | 1189-1719-ND | Rubycon | 16PK1000MEFC10X12.5
0.1" headers 40 pin strips | https://www.amazon.com/Header-Lystaii-Pin-Connector-Electronic/dp/B06ZZN8L9S/ | $0.09 | 3 | $0.27 | Amazon | B06ZZN8L9S | Lystaii
arduino-to-headers-shield 53.34 mm x 70.78 mm (2.1" x 2.79") |  | $1.82 | 1 | $1.82 | PCBWay
 |  |  |  |  |  | $0.00

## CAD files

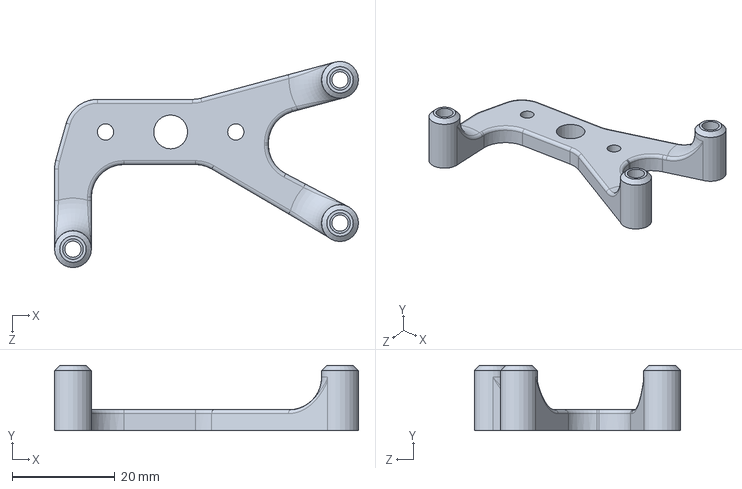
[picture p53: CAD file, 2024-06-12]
3dprint/arduino-bracket.SLDPRT
59.3 x 12.7 x 40.2 mm

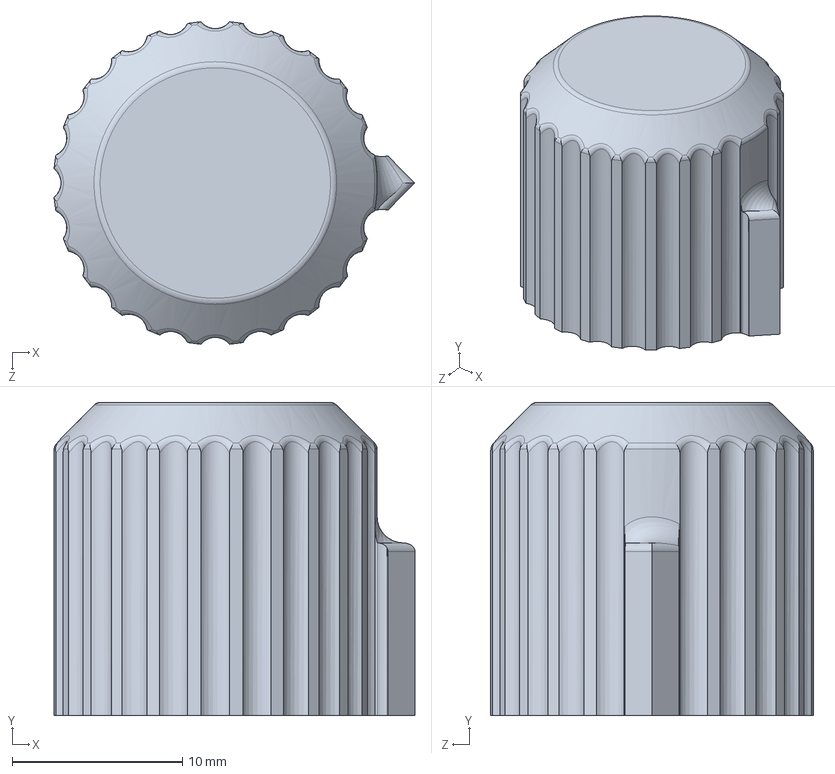
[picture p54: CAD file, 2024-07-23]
bud-box/knob.SLDPRT
21.2 x 18.4 x 19.0 mm

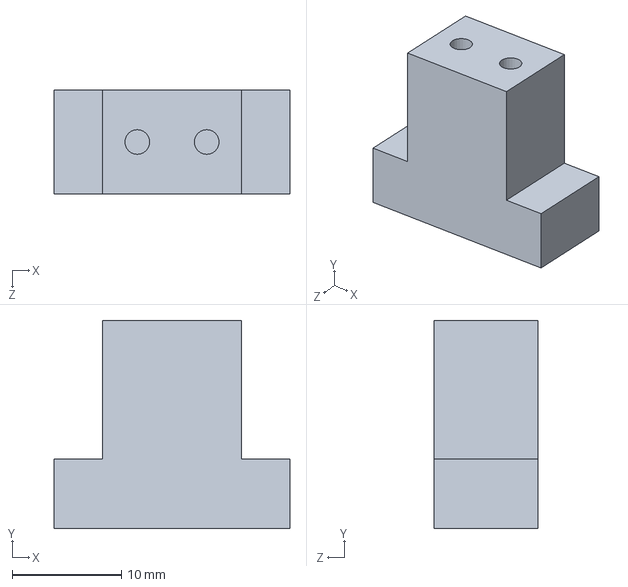
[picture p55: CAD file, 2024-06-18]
cold-mechanical/standoff.SLDPRT
21.6 x 19.0 x 9.53 mm

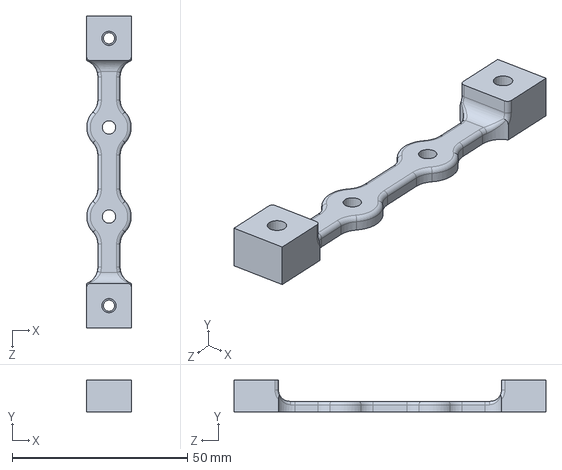
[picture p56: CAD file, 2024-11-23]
front-panel-edge-bracket.SLDPRT
12.7 x 9.00 x 88.9 mm

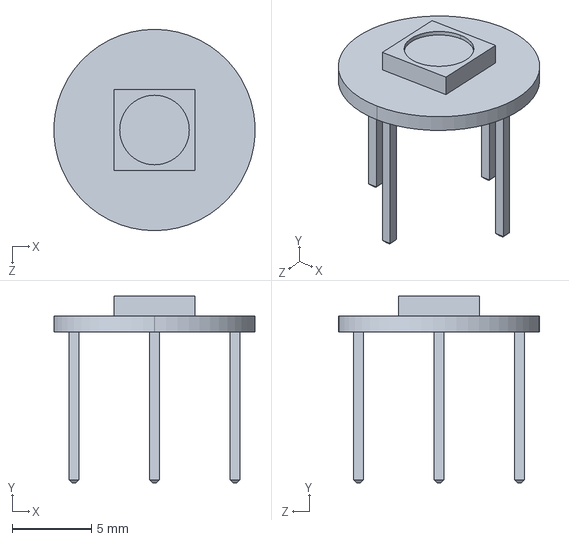
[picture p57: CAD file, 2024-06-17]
pcb/9button-9neopixels/half-inch-round-neopixel-board.STEP
12.7 x 11.8 x 12.7 mm

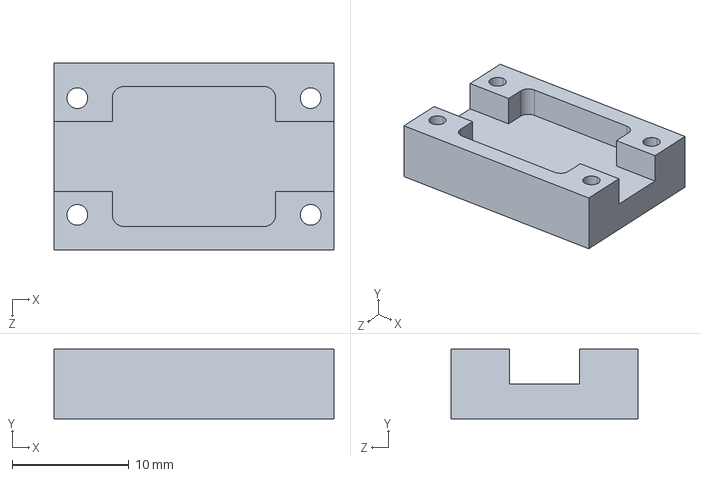
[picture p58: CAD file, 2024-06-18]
pcb/calboards/chip-house.STEP
24.0 x 6.00 x 16.0 mm

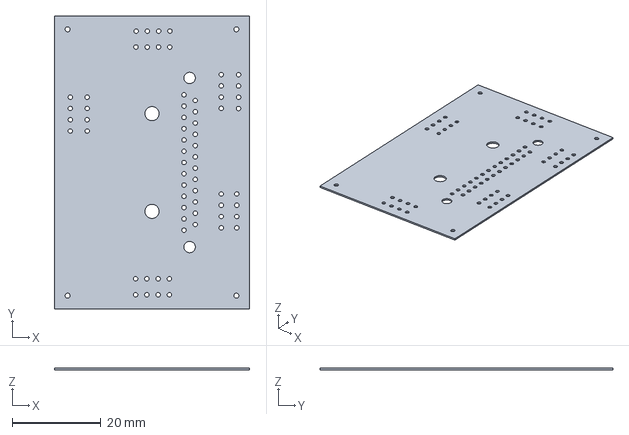
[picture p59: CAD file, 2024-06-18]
pcb/microd-header-adapter-board-rev2/microd-header-adapter-board-rev2.step
44.0 x 66.0 x 0.411 mm

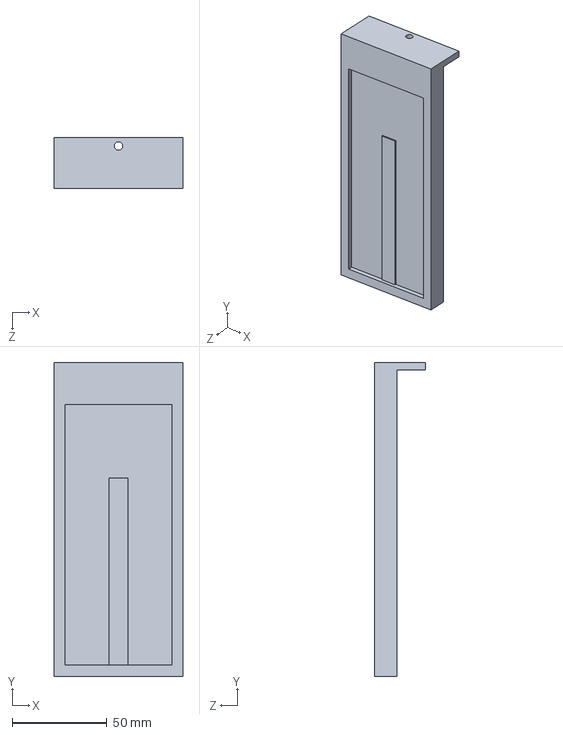
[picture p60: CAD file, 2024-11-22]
1x9x1-mounting-bracket.SLDPRT
68.0 x 166.0 x 27.0 mm

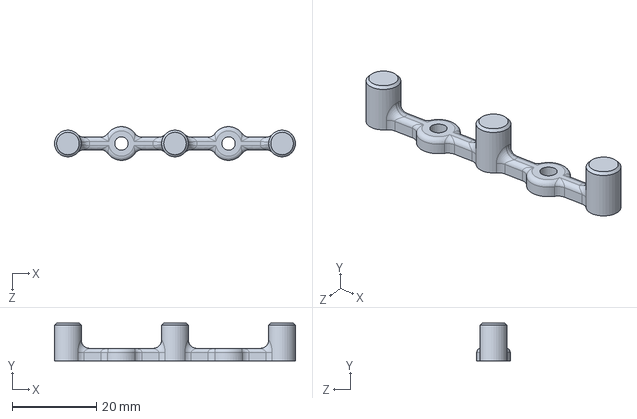
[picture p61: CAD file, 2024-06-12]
3dprint/front-panel-center-bracket.SLDPRT
57.1 x 9.00 x 7.98 mm

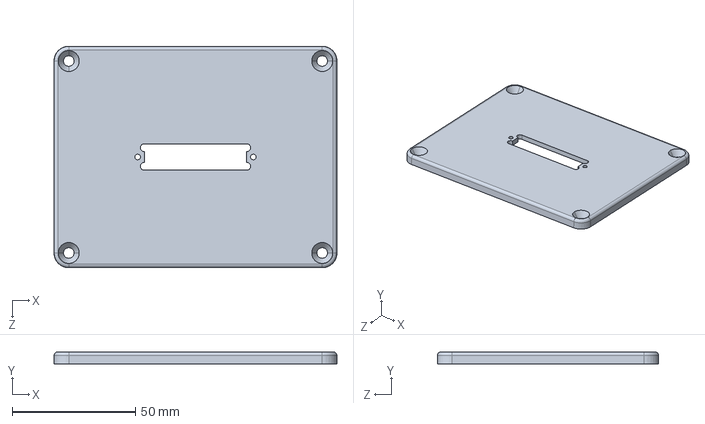
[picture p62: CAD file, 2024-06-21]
bud-box/AN-1304-A-lid-machined.STEP
115.0 x 5.00 x 90.0 mm

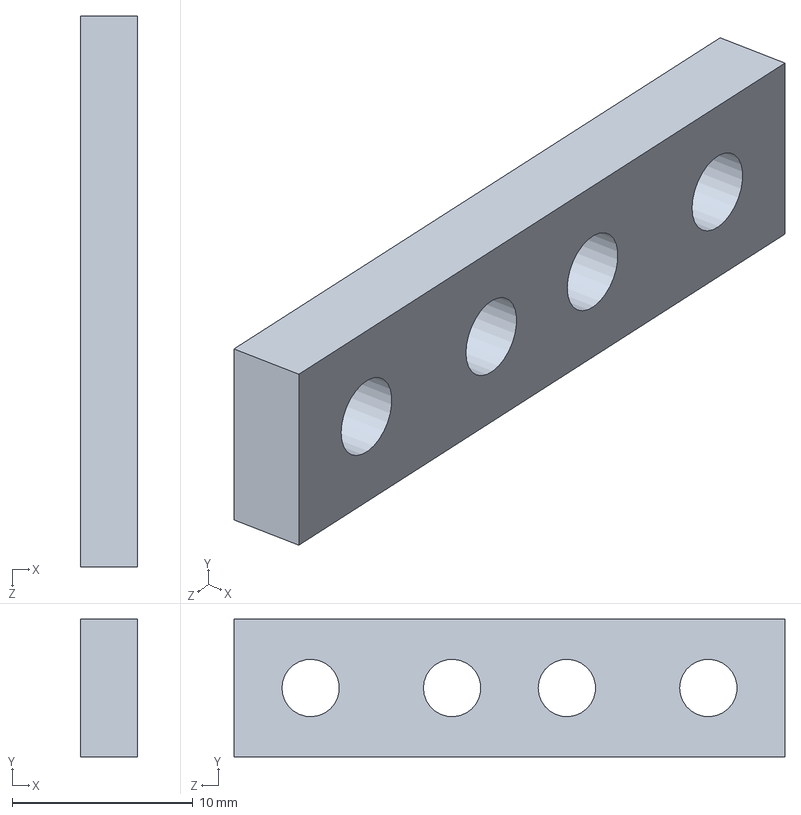
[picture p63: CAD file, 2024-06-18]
cold-mechanical/center-block-outside.SLDPRT
3.17 x 7.62 x 30.5 mm

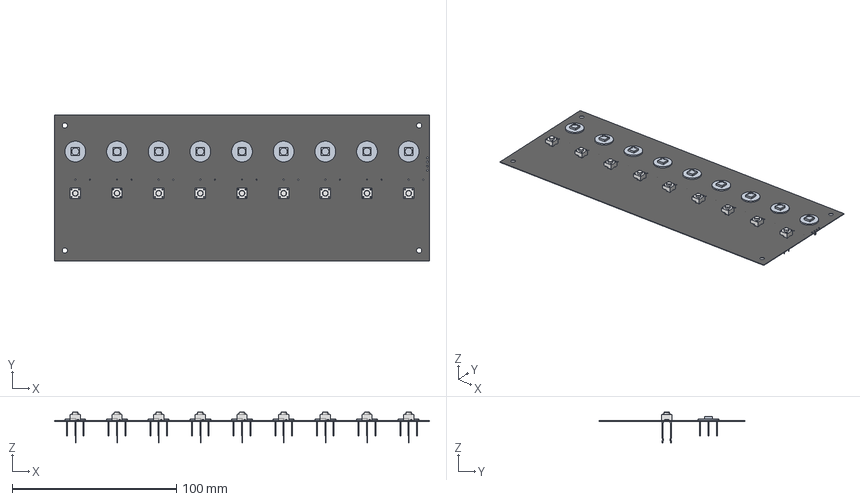
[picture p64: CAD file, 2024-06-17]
pcb/9button-9neopixels/9button-9neopixel.step
228.6 x 88.9 x 18.6 mm
TL59AF100Q x 9
half-inch-round-neopixel-board x 9

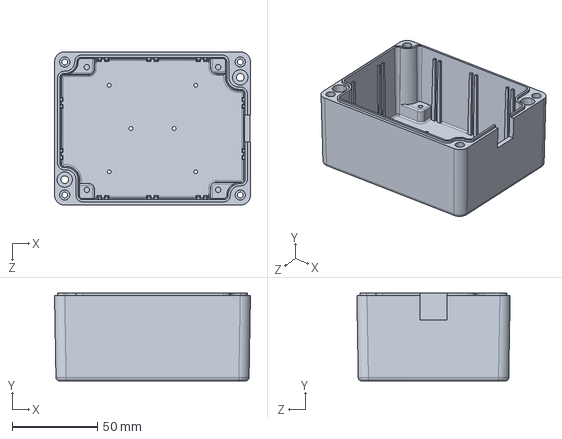
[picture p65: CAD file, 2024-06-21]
bud-box/AN-1304-A-machined-box.STEP
115.0 x 51.5 x 90.0 mm

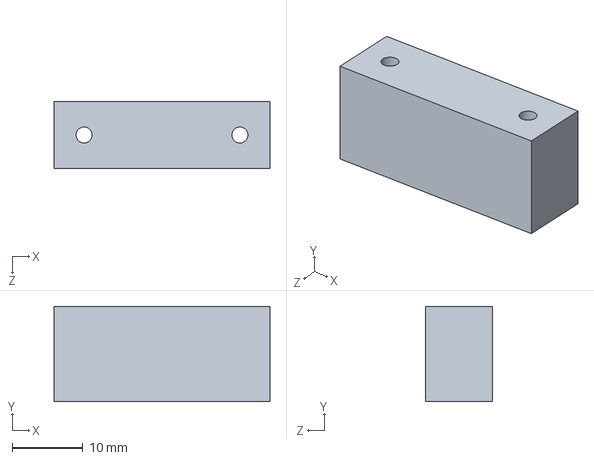
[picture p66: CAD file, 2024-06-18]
cold-mechanical/center-block-v2.SLDPRT
30.5 x 13.4 x 9.53 mm

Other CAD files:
1x9x1assembly.SLDASM
coldAssembly.SLDASM
1x9x1.step
cold-mechanical/HBracket-M4.SLDPRT
1.9in Coupler Module.stp
1.9in Coupler Module.stp.SLDPRT
1x9x1.SLDDRW
1x9x1.SLDPRT
1x9x1.step.SLDPRT
2-292161-4_TYC.step
3dprint/arduino-bracket.STL
3dprint/front-panel-center-bracket.STL
3dprint/front-panel-edge-bracket.SLDPRT
3dprint/front-panel-edge-bracket.STL
AN-1304-A-box-modifications.SLDDRW
AN-1304-A-box-modifications.SLDPRT
AN-1304-A-lid-modifications.SLDDRW
AN-1304-A-lid-modifications.SLDPRT
CAP_PKPZ_10X12P5_LOW_RUB.step
CryoElec_SP3T_SMA_3D_Model.step
HV-DCDC-bracket.SLDDRW
HV-DCDC-bracket.SLDPRT
HV-DCDC-bracket.STL
arduino-bracket.SLDDRW
arduino-bracket.SLDPRT
bud-box/AN-1304-A-lid-machined.SLDDRW
bud-box/AN-1304-A-machined-box.SLDDRW
bud-box/knob.STL
cold-mechanical/HBracket-M4.SLDDRW
cold-mechanical/center-block-outside.SLDDRW
cold-mechanical/center-block-v2.SLDDRW
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

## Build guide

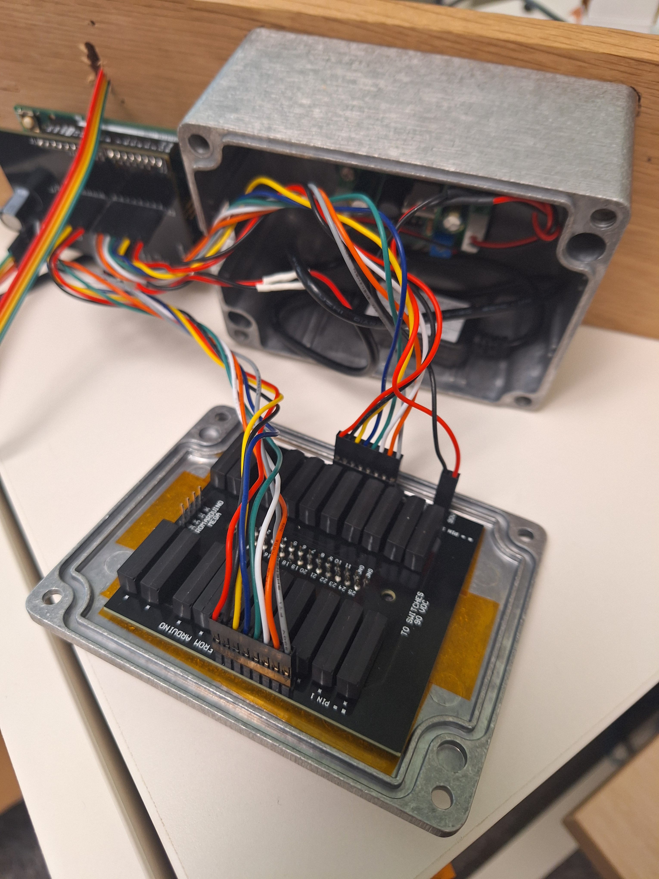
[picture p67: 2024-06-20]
images/back-disassembly.jpg

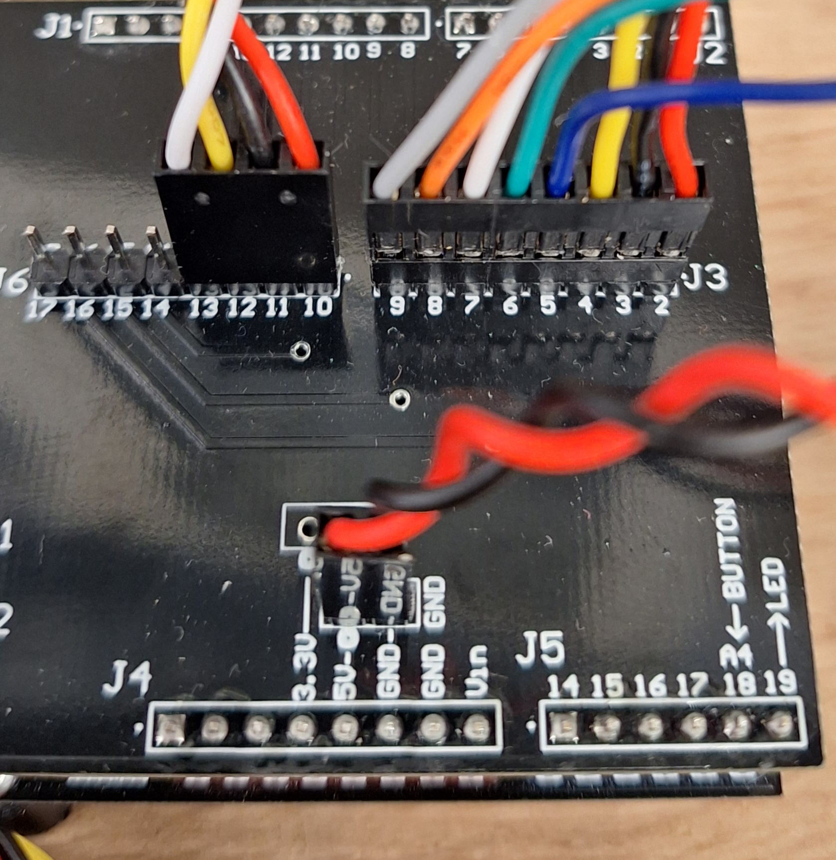
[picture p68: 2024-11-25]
images/shield-cable-wiring.png

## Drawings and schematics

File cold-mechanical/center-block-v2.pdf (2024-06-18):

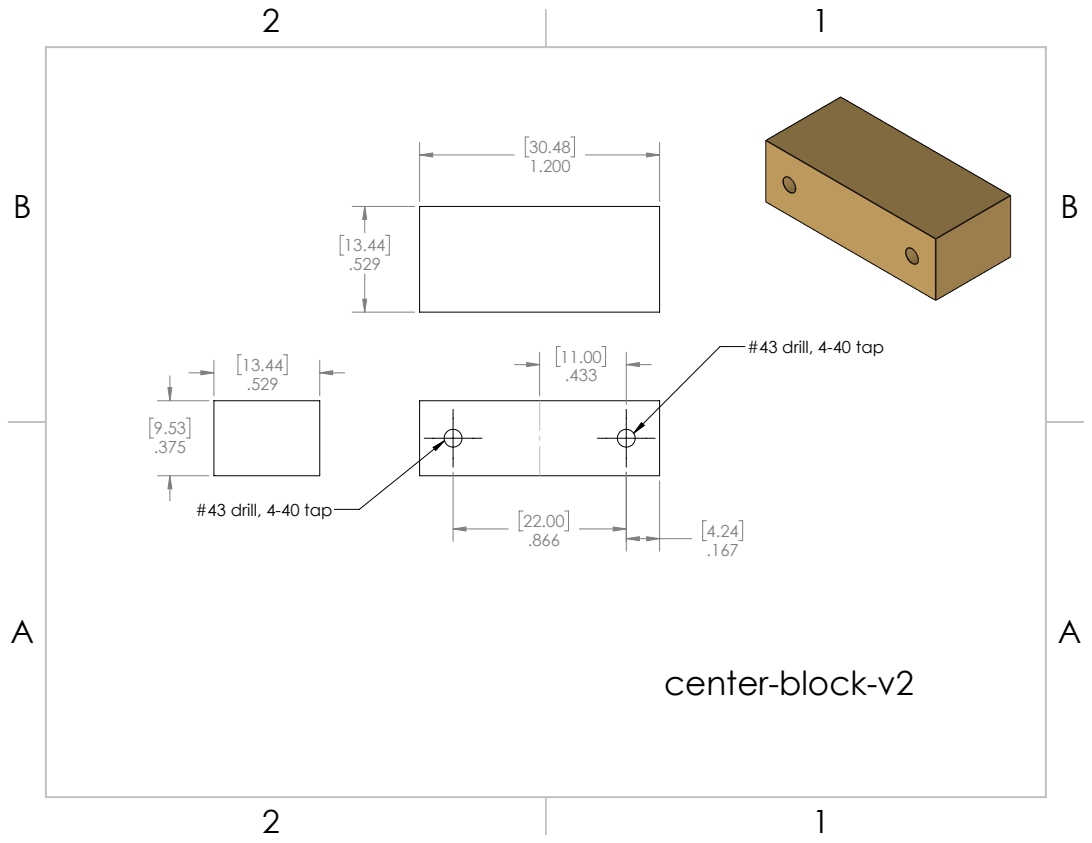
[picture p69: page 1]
#43 drill, 4-40 tap

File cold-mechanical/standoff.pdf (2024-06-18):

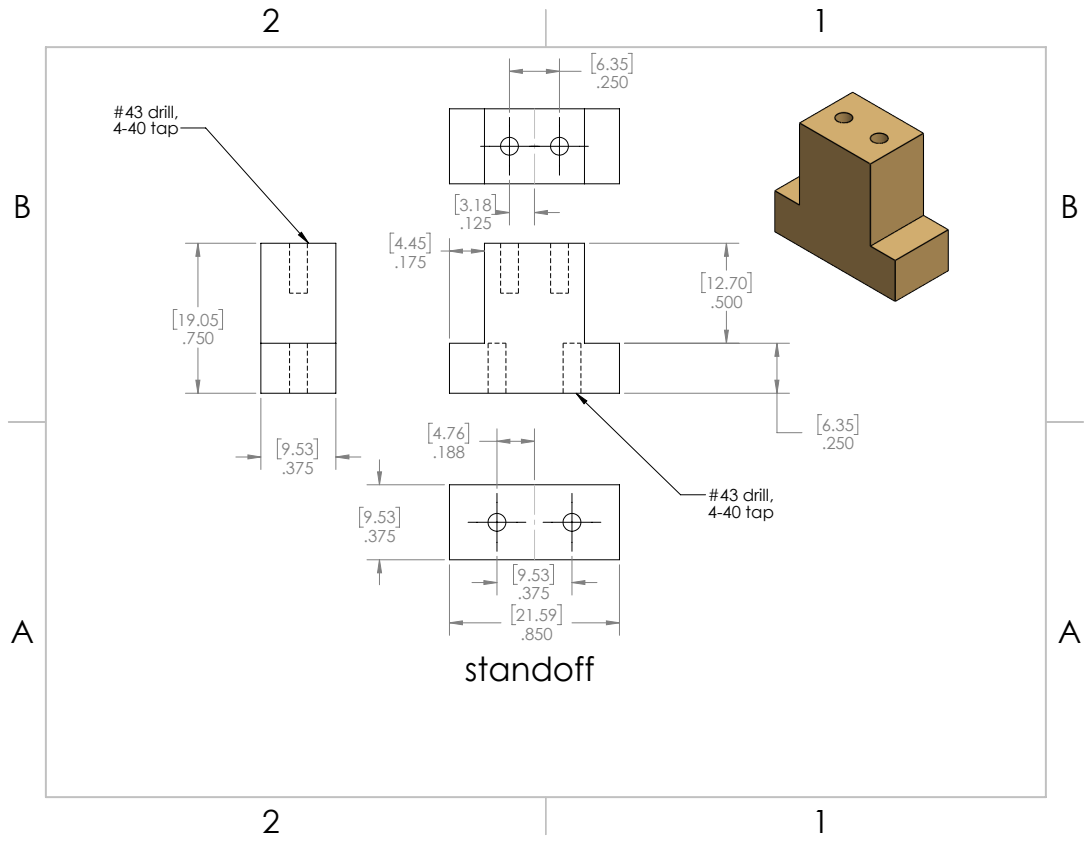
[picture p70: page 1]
#43 drill, 4-40 tap

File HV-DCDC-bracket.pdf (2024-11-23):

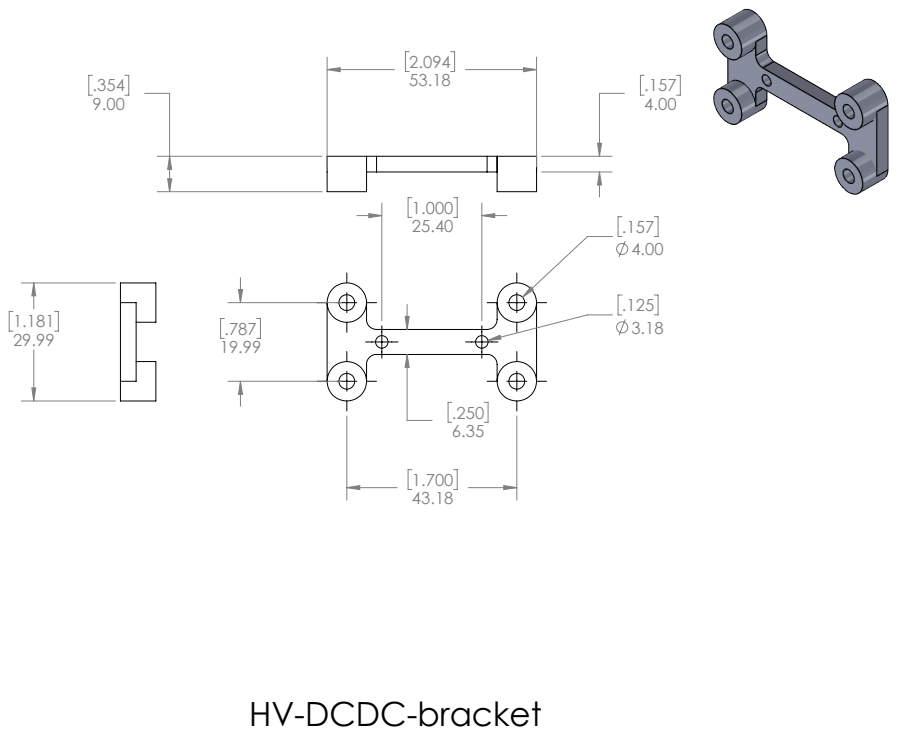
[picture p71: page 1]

HV-DCDC-bracket

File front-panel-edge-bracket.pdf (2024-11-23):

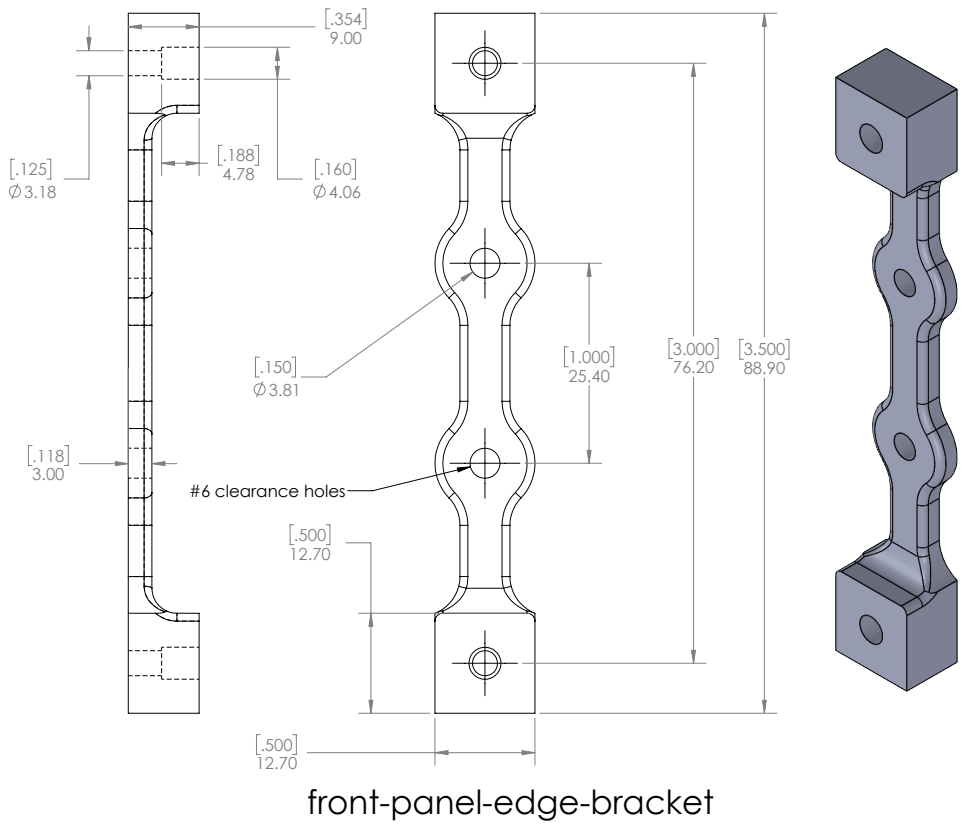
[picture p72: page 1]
#6 clearance holes

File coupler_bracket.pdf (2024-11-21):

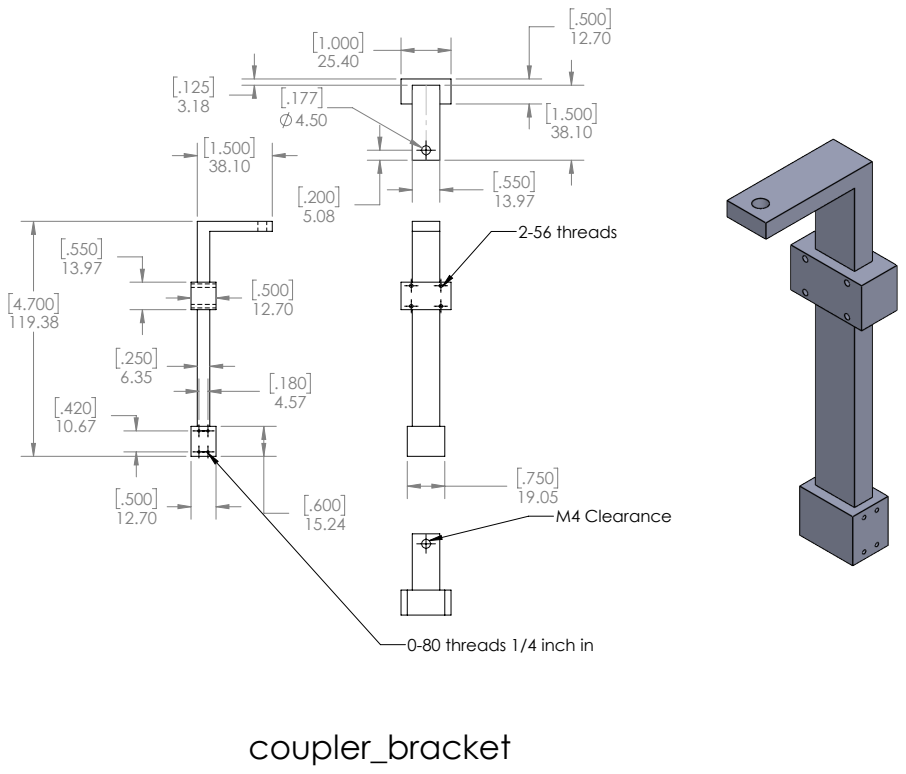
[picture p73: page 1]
2-56 threads; M4 Clearance

0-80 threads 1/4 inch in

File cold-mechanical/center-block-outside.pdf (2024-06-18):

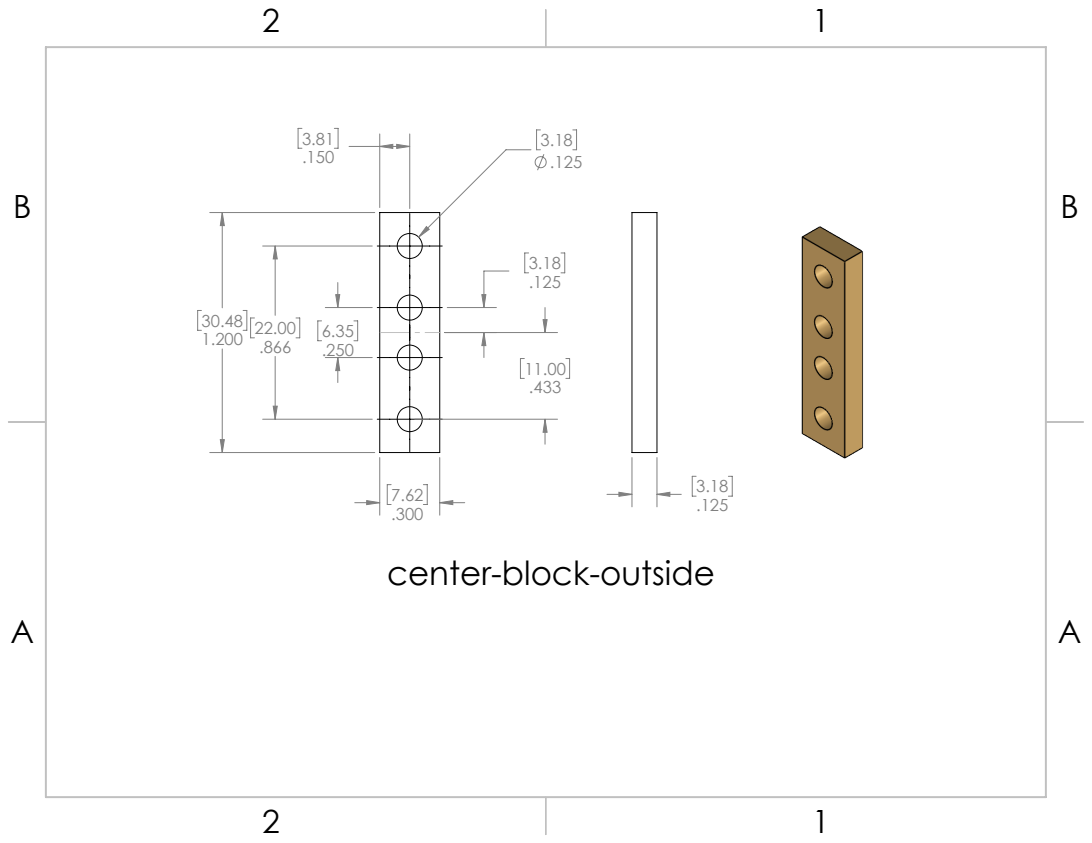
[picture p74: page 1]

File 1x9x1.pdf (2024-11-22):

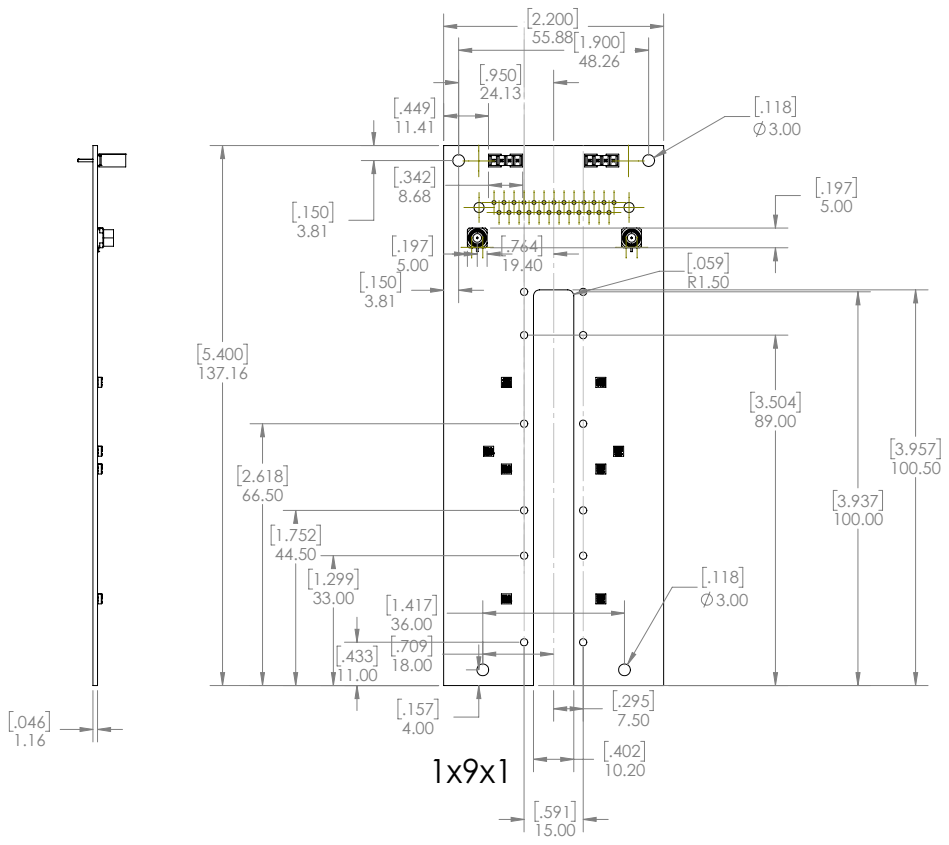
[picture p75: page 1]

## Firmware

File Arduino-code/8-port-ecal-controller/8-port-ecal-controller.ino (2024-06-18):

#include <Adafruit_NeoPixel.h>
#ifdef __AVR__
#endif

// Which pin on the Arduino is connected to the NeoPixels?
#define PIN 59 // On Trinket or Gemma, suggest changing this to 1

// How many NeoPixels are attached to the Arduino?
#define NUMPIXELS 12 // 
//there are 9

// When setting up the NeoPixel library, we tell it how many pixels,  
// and which pin to use to send signals. Note that for older NeoPixel
// strips you might need to change the third parameter -- see the
// strandtest example for more information on possible values.
Adafruit_NeoPixel pixels(NUMPIXELS, PIN, NEO_GRB + NEO_KHZ800);

#define SP8T_1 2
#define SP8T_2 3
#define SP8T_3 4
#define SP8T_4 5

#define SP8T_5 6
#define SP8T_6 7
#define SP8T_7 8
#define SP8T_8 9

#define NOT_SP8T_1 10
#define NOT_SP8T_2 11
#define NOT_SP8T_3 12
#define NOT_SP8T_4 13

#define NOT_SP8T_5 14
#define NOT_SP8T_6 15
#define NOT_SP8T_7 16
#define NOT_SP8T_8 17

#define ECAL_SHORT 30
#define ECAL_LOAD 32
#define ECAL_1234 34
#define ECAL_5678 36

int analog = 0;
int analogEcal = 0;
int delta = 20;
int mode = 1;//modes are 1,2,3,4,5,6,7,8 which are pixel 7,6,5,4,3,2,1, and 0 respectively
int modeEcal = 4;//modes are 1,2,3,4 which are pixel 3,2,1, and 0 respectively. mode 1 is short, 2 is open, 3 is load, 4 is thru


void setup() {
    Serial.begin(115200);


  // These lines are specifically to support the Adafruit Trinket 5V 16 MHz.
  // Any other board, you can remove this part (but no harm leaving it):
#if defined(__AVR_ATtiny85__) && (F_CPU == 16000000)
  clock_prescale_set(clock_div_1);
#endif
  // END of Trinket-specific code.

/*
    pinMode(2,OUTPUT);// DSUB 8,  U4 -> U1
    pinMode(3,OUTPUT);// DSUB 9,  U4 -> U2
    pinMode(4,OUTPUT);// DSUB 10, U4 -> U3
    pinMode(5,OUTPUT);// DSUB 11, U4 COM
    pinMode(6,OUTPUT);// DSUB 14, U3 -> port 7
    pinMode(7,OUTPUT);// DSUB 15, U3 -> port 8
    pinMode(8,OUTPUT);// DSUB 16, U3 -> port 9
    pinMode(9,OUTPUT);// DSUB 17, U3 COM
    pinMode(10,OUTPUT);//DSUB 18, U2 -> 4 
    pinMode(11,OUTPUT);//DSUB 19, U2 -> 5
    pinMode(12,OUTPUT);//DSUB 20, U2 -> 6
    pinMode(13,OUTPUT);//DSUB 21, U2 COM
    pinMode(14,OUTPUT);//DSUB 22, U1 -> 1
    pinMode(15,OUTPUT);//DSUB 23, U1 -> 2
    pinMode(16,OUTPUT);//DSUB 24, U1 -> 3
    pinMode(17,OUTPUT);//DSUB 25, U1 COM
*/

    pinMode(SP8T_1,OUTPUT);
    pinMode(SP8T_2,OUTPUT);
    pinMode(SP8T_3,OUTPUT);
    pinMode(SP8T_4,OUTPUT);
    pinMode(SP8T_5,OUTPUT);
    pinMode(SP8T_6,OUTPUT);
    pinMode(SP8T_7,OUTPUT);
    pinMode(SP8T_8,OUTPUT);

    pinMode(NOT_SP8T_1,OUTPUT);
    pinMode(NOT_SP8T_2,OUTPUT);
    pinMode(NOT_SP8T_3,OUTPUT);
    pinMode(NOT_SP8T_4,OUTPUT);
    pinMode(NOT_SP8T_5,OUTPUT);
    pinMode(NOT_SP8T_6,OUTPUT);
    pinMode(NOT_SP8T_7,OUTPUT);
    pinMode(NOT_SP8T_8,OUTPUT);

    pinMode(ECAL_SHORT,OUTPUT);
    pinMode(ECAL_LOAD,OUTPUT);
    pinMode(ECAL_1234,OUTPUT);
    pinMode(ECAL_5678,OUTPUT);

    digitalWrite(SP8T_1,LOW);
    digitalWrite(SP8T_2,LOW);
    digitalWrite(SP8T_3,LOW);
    digitalWrite(SP8T_4,LOW);
    digitalWrite(SP8T_5,LOW);
    digitalWrite(SP8T_6,LOW);
    digitalWrite(SP8T_7,LOW);
    digitalWrite(SP8T_8,LOW);

    digitalWrite(NOT_SP8T_1,LOW);
    digitalWrite(NOT_SP8T_2,LOW);
    digitalWrite(NOT_SP8T_3,LOW);
    digitalWrite(NOT_SP8T_4,LOW);
    digitalWrite(NOT_SP8T_5,LOW);
    digitalWrite(NOT_SP8T_6,LOW);
    digitalWrite(NOT_SP8T_7,LOW);
    digitalWrite(NOT_SP8T_8,LOW);

    digitalWrite(ECAL_SHORT,LOW);
    digitalWrite(ECAL_LOAD,LOW);
    digitalWrite(ECAL_1234,HIGH);
    digitalWrite(ECAL_5678,LOW);


  pixels.begin(); // INITIALIZE NeoPixel strip object (REQUIRED)

}





void loop() {

    

  pixels.clear(); // Set all pixel colors to 'off'
  analog = analogRead(A8);

  // The first NeoPixel in a strand is #0, second is 1, all the way up
  // to the count of pixels minus one.
  
  if(analog > 1023 - delta){
    delay(1);
    analog = analogRead(A8);
    if(analog > 1023 - delta){
       mode = 1;      
    }
  }
  if(analog > 822 - delta && analog < 822 + delta){
    delay(5);
    analog = analogRead(A8);
    if(analog > 822 - delta && analog < 822 + delta){
         mode = 2; 
    }
  }
  if(analog > 667 - delta && analog < 667 + delta){
     delay(5);
     analog = analogRead(A8);

    if(analog > 667 - delta && analog < 667 + delta){
      mode = 3;    
    }
  }

  if(analog > 538 - delta && analog < 538 + delta){
     delay(1);
     analog = analogRead(A8);

    if(analog > 538 - delta && analog < 538 + delta){
      mode = 4;    
    }
  }

  if(analog > 425 - delta && analog < 425 + delta){
     delay(1);
     analog = analogRead(A8);

    if(analog > 425 - delta && analog < 425 + delta){
      mode = 5;    
    }
  }

  if(analog > 321 - delta && analog < 321 + delta){
     delay(1);
     analog = analogRead(A8);

    if(analog > 321 - delta && analog < 321 + delta){
      mode = 6;    
    }
  }

  if(analog > 220 - delta && analog < 220 + delta){
     delay(1);
     analog = analogRead(A8);

    if(analog > 220 - delta && analog < 220 + delta){
      mode = 7;    
    }
  }

  if(analog > 115 - delta && analog < 115 + delta){
     delay(1);
     analog = analogRead(A8);

    if(analog > 115 - delta && analog < 115 + delta){
      mode = 8;    
    }
  }

  analogEcal = analogRead(A4);

  if(analogEcal > 1023 - delta){
    delay(1);
    analog = analogRead(A4);
    if(analogEcal > 1023 - delta){
       modeEcal = 1;      
    }
  }

  if(analogEcal > 714 - delta && analogEcal < 714 + delta){
     delay(1);
     analogEcal = analogRead(A4);
    if(analogEcal > 714 - delta && analogEcal < 714 + delta){
      modeEcal = 2;    
    }
  }

  if(analogEcal > 463 - delta && analogEcal < 463 + delta){
     delay(1);
     analogEcal = analogRead(A4);
    if(analogEcal > 463 - delta && analogEcal < 463 + delta){
      modeEcal = 3;    
    }
  }

  if(analogEcal > 236 - delta && analogEcal < 236 + delta){
     delay(1);
     analogEcal = analogRead(A4);
    if(analogEcal > 236 - delta && analogEcal < 236 + delta){
      modeEcal = 4;    
    }
  }

  if (Serial.available()) {

    //for more info on this code see http://adam-meyer.com/arduino/arduino-serial
    //read serial as ascii integer
     int ser = Serial.read();
    //    Serial.println(ser);
     if(ser == 49){    //ASCII for 1
      mode = 1;
     }
     if(ser == 50){    //ASCII for 2
      mode = 2;
     }
     if(ser == 51){    //ASCII for 3
      mode = 3;
     }
     if(ser == 52){    //ASCII for 4
      mode = 4;
     }
     if(ser == 53){    //ASCII for 5
      mode = 5;
     }
     if(ser == 54){    //ASCII for 6
      mode = 6;
     }
     if(ser == 55){    //ASCII for 4
      mode = 7;
     }
     if(ser == 56){    //ASCII for 5
      mode = 8;
     }
 
     if(ser == 115){    //ASCII for s
      modeEcal = 1;
     }
     if(ser == 111){    //ASCII for o
      modeEcal = 2;
     }
     if(ser == 108){    //ASCII for l
      modeEcal = 3;
     }
     if(ser == 116){    //ASCII for t
      modeEcal = 4;
     }


  }

  if(mode == 1){
   
    pixels.setPixelColor(4, pixels.Color(0, 0, 0));    
    pixels.setPixelColor(5, pixels.Color(0, 0, 0));    
    pixels.setPixelColor(6, pixels.Color(0, 0, 0));    
    pixels.setPixelColor(7, pixels.Color(0, 0, 0));    
    pixels.setPixelColor(8, pixels.Color(0, 0, 0));    
    pixels.setPixelColor(9, pixels.Color(0, 0, 0));    
    pixels.setPixelColor(10, pixels.Color(0, 0, 0));    
    pixels.setPixelColor(11, pixels.Color(100, 0, 100));    



    digitalWrite(SP8T_1,HIGH);
    digitalWrite(SP8T_2,LOW);
    digitalWrite(SP8T_3,LOW);
    digitalWrite(SP8T_4,LOW);
    digitalWrite(SP8T_5,LOW);
    digitalWrite(SP8T_6,LOW);
    digitalWrite(SP8T_7,LOW);
    digitalWrite(SP8T_8,LOW);

    digitalWrite(NOT_SP8T_1,LOW);
    digitalWrite(NOT_SP8T_2,HIGH);
    digitalWrite(NOT_SP8T_3,HIGH);
    digitalWrite(NOT_SP8T_4,HIGH);
    digitalWrite(NOT_SP8T_5,HIGH);
    digitalWrite(NOT_SP8T_6,HIGH);
    digitalWrite(NOT_SP8T_7,HIGH);
    digitalWrite(NOT_SP8T_8,HIGH);
    
  }
  if(mode == 2){

    pixels.setPixelColor(4, pixels.Color(0, 0, 0));    
    pixels.setPixelColor(5, pixels.Color(0, 0, 0));    
    pixels.setPixelColor(6, pixels.Color(0, 0, 0));    
    pixels.setPixelColor(7, pixels.Color(0, 0, 0));    
    pixels.setPixelColor(8, pixels.Color(0, 0, 0));    
    pixels.setPixelColor(9, pixels.Color(0, 0, 0));    
    pixels.setPixelColor(10, pixels.Color(100, 0, 100));    
    pixels.setPixelColor(11, pixels.Color(0, 0, 0)); 
    
    digitalWrite(SP8T_1,LOW);
    digitalWrite(SP8T_2,HIGH);
    digitalWrite(SP8T_3,LOW);
    digitalWrite(SP8T_4,LOW);
    digitalWrite(SP8T_5,LOW);
    digitalWrite(SP8T_6,LOW);
    digitalWrite(SP8T_7,LOW);
    digitalWrite(SP8T_8,LOW);

    digitalWrite(NOT_SP8T_1,HIGH);
    digitalWrite(NOT_SP8T_2,LOW);
    digitalWrite(NOT_SP8T_3,HIGH);
    digitalWrite(NOT_SP8T_4,HIGH);
    digitalWrite(NOT_SP8T_5,HIGH);
    digitalWrite(NOT_SP8T_6,HIGH);
    digitalWrite(NOT_SP8T_7,HIGH);
    digitalWrite(NOT_SP8T_8,HIGH);
  }
  if(mode == 3){
  
    pixels.setPixelColor(4, pixels.Color(0, 0, 0));    
    pixels.setPixelColor(5, pixels.Color(0, 0, 0));    
    pixels.setPixelColor(6, pixels.Color(0, 0, 0));    
    pixels.setPixelColor(7, pixels.Color(0, 0, 0));    
    pixels.setPixelColor(8, pixels.Color(0, 0, 0));    
    pixels.setPixelColor(9, pixels.Color(100, 0, 100));    
    pixels.setPixelColor(10, pixels.Color(0, 0, 0));    
    pixels.setPixelColor(11, pixels.Color(0, 0, 0));    
        
    digitalWrite(SP8T_1,LOW);
    digitalWrite(SP8T_2,LOW);
    digitalWrite(SP8T_3,HIGH);
    digitalWrite(SP8T_4,LOW);
    digitalWrite(SP8T_5,LOW);
    digitalWrite(SP8T_6,LOW);
    digitalWrite(SP8T_7,LOW);
    digitalWrite(SP8T_8,LOW);

    digitalWrite(NOT_SP8T_1,HIGH);
    digitalWrite(NOT_SP8T_2,HIGH);
    digitalWrite(NOT_SP8T_3,LOW);
    digitalWrite(NOT_SP8T_4,HIGH);
    digitalWrite(NOT_SP8T_5,HIGH);
    digitalWrite(NOT_SP8T_6,HIGH);
    digitalWrite(NOT_SP8T_7,HIGH);
    digitalWrite(NOT_SP8T_8,HIGH);
  }
  if(mode == 4){

    pixels.setPixelColor(4, pixels.Color(0, 0, 0));    
    pixels.setPixelColor(5, pixels.Color(0, 0, 0));    
    pixels.setPixelColor(6, pixels.Color(0, 0, 0));    
    pixels.setPixelColor(7, pixels.Color(0, 0, 0));    
    pixels.setPixelColor(8, pixels.Color(100, 0, 100));    
    pixels.setPixelColor(9, pixels.Color(0, 0, 0));    
    pixels.setPixelColor(10, pixels.Color(0, 0, 0));    
    pixels.setPixelColor(11, pixels.Color(0, 0, 0)); 

    digitalWrite(SP8T_1,LOW);
    digitalWrite(SP8T_2,LOW);
    digitalWrite(SP8T_3,LOW);
    digitalWrite(SP8T_4,HIGH);
    digitalWrite(SP8T_5,LOW);
    digitalWrite(SP8T_6,LOW);
    digitalWrite(SP8T_7,LOW);
    digitalWrite(SP8T_8,LOW);

    digitalWrite(NOT_SP8T_1,HIGH);
    digitalWrite(NOT_SP8T_2,HIGH);
    digitalWrite(NOT_SP8T_3,HIGH);
    digitalWrite(NOT_SP8T_4,LOW);
    digitalWrite(NOT_SP8T_5,HIGH);
    digitalWrite(NOT_SP8T_6,HIGH);
    digitalWrite(NOT_SP8T_7,HIGH);
    digitalWrite(NOT_SP8T_8,HIGH);    

  }
  if(mode == 5){

    pixels.setPixelColor(4, pixels.Color(0, 0, 0));    
    pixels.setPixelColor(5, pixels.Color(0, 0, 0));    
    pixels.setPixelColor(6, pixels.Color(0, 0, 0));    
    pixels.setPixelColor(7, pixels.Color(100, 0, 100));    
    pixels.setPixelColor(8, pixels.Color(0, 0, 0));    
    pixels.setPixelColor(9, pixels.Color(0, 0, 0));    
    pixels.setPixelColor(10, pixels.Color(0, 0, 0));    
    pixels.setPixelColor(11, pixels.Color(0, 0, 0));   
    
    digitalWrite(SP8T_1,LOW);
    digitalWrite(SP8T_2,LOW);
    digitalWrite(SP8T_3,LOW);
    digitalWrite(SP8T_4,LOW);
    digitalWrite(SP8T_5,HIGH);
    digitalWrite(SP8T_6,LOW);
    digitalWrite(SP8T_7,LOW);
    digitalWrite(SP8T_8,LOW);
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

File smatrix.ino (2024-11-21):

/*

4 buttons set 4 s paramters in this order: S11, S22, S21, S12

*/



#include <Adafruit_NeoPixel.h>
#ifdef __AVR__
#endif

// Which pin on the Arduino is connected to the NeoPixels?
#define PIN 19 // A5 on UNO is pin 19

// How many NeoPixels are attached to the Arduino?
#define NUMPIXELS 9 // 
//there are 9

// When setting up the NeoPixel library, we tell it how many pixels,  
// and which pin to use to send signals. Note that for older NeoPixel
// strips you might need to change the third parameter -- see the
// strandtest example for more information on possible values.
Adafruit_NeoPixel pixels(NUMPIXELS, PIN, NEO_GRB + NEO_KHZ800);

#define OUTPUT_SWITCH_RFC 5
#define OUTPUT_SWITCH_RF1 4
#define OUTPUT_SWITCH_RF2 3
#define OUTPUT_SWITCH_RF3 2

#define INPUT_SWITCH_RFC 9
#define INPUT_SWITCH_RF1 8
#define INPUT_SWITCH_RF2 7
#define INPUT_SWITCH_RF3 6


int analog = 0;
int delta = 20;
int mode = 1;//modes are 1,2,3,4,5,6,7,8,9 which are pixel 8,7,6,5,4,3,2,1, and 0 respectively
int cycle = 0;//variable for cycling colors as test pattern with switch off

//input and output = 1 is S21, input and output = 2 is S22, S21 is from port 1 to port 2, and is input 1 and output 2
int inputselect = 1;
int outputselect = 1;

String sparameter = "Hello String";  

//modes are 

void setup() {
    Serial.begin(9600);

    pinMode(OUTPUT_SWITCH_RFC,OUTPUT);
    pinMode(OUTPUT_SWITCH_RF1,OUTPUT);
    pinMode(OUTPUT_SWITCH_RF2,OUTPUT);
    pinMode(OUTPUT_SWITCH_RF3,OUTPUT);

    pinMode(INPUT_SWITCH_RFC,OUTPUT);
    pinMode(INPUT_SWITCH_RF1,OUTPUT);
    pinMode(INPUT_SWITCH_RF2,OUTPUT);
    pinMode(INPUT_SWITCH_RF3,OUTPUT);

    digitalWrite(OUTPUT_SWITCH_RFC,HIGH);
    digitalWrite(INPUT_SWITCH_RFC,HIGH);
    digitalWrite(INPUT_SWITCH_RF2,LOW);
    digitalWrite(OUTPUT_SWITCH_RF2,LOW);

    digitalWrite(OUTPUT_SWITCH_RF1,HIGH);
    digitalWrite(OUTPUT_SWITCH_RF3,LOW);
    digitalWrite(INPUT_SWITCH_RF1,HIGH);
    digitalWrite(INPUT_SWITCH_RF3,LOW);
  
  pixels.begin(); // INITIALIZE NeoPixel strip object (REQUIRED)

}





void loop() {

    

  pixels.clear(); // Set all pixel colors to 'off'
  analog = analogRead(A4);
  // The first NeoPixel in a strand is #0, second is 1, all the way up
  // to the count of pixels minus one.
  
  if(analog > 1024 - delta){
    delay(1);
    analog = analogRead(A4);
    if(analog > 1023 - delta){
      outputselect = 1;
      inputselect = 1;
    }
  }
  if(analog > 836 - delta && analog < 836 + delta){
    delay(5);
    analog = analogRead(A4);
    if(analog > 836 - delta && analog < 836 + delta){
      outputselect = 2;
      inputselect = 2;
    }
  }
  if(analog > 690 - delta && analog < 690 + delta){
     delay(5);
     analog = analogRead(A4);

    if(analog > 690 - delta && analog < 690 + delta){
      outputselect = 2;
      inputselect = 1;
    }
  }

  if(analog > 569 - delta && analog < 569 + delta){
     delay(1);
     analog = analogRead(A4);

    if(analog > 569 - delta && analog < 569 + delta){
      outputselect = 1;
      inputselect = 2;
    }
  }


  if(analog > 464 - delta && analog < 464 + delta){
     delay(1);
     analog = analogRead(A4);

    if(analog > 464 - delta && analog < 464 + delta){
      //mode = 5;    
    }
  }
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

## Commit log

2024-06-12 QNA creation
    [HV-DCDC-bracket.SLDPRT, HV-DCDC-bracket.STL, arduino-bracket.SLDPRT, arduino-bracket.STL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]
2024-06-12 images for 3d print files
2024-06-12 images of wood boards
2024-06-13 arduino code
2024-06-13 fixed thickness of base plate in HV holder bracket
    [HV-DCDC-bracket.SLDPRT, HV-DCDC-bracket.STL]
2024-06-17 all the files for the 9 button front panel board
    [9button-9neopixel.PcbDoc, 9button-9neopixel.SLDDRW, 9button-9neopixel.SLDPRT, 9button-9neopixel.SchDoc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]
2024-06-18 build arduino code for ecal, added images of more pcb's
    [arduino-to-headers-shield.PcbDoc, arduino-to-headers-shield.PrjPcb, arduino-to-headers-shield.SchDoc]
2024-06-18 put together all the pcb designs
    [10cm-chip-cal-board-1point2in.PcbDoc, 10cm-chip-cal-board-1point2in.PrjPcb, 10cm-chip-cal-board-1point2in.SchDoc, DB25-relay-HV-control.PcbDoc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]
2024-06-18 cold mechanicals files added
    [HBracket-M4.SLDDRW, HBracket-M4.SLDPRT, center-block-outside.SLDDRW, center-block-outside.SLDPRT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]
2024-06-20 images of system components
    [cal-boards-panelization1.PcbDoc, cal-boards-panelization2.PcbDoc]
2024-06-20 pcb replicator
2024-06-20 building front panel board replicator
2024-06-20 more pcb docs
2024-06-21 relay board replicator construction
2024-06-21 relay board assembly replicators
2024-06-21 micro D header breakout board docs
2024-06-21 cold breakout board replicator
2024-06-21 3d print docs and replicators
2024-06-21 3d print docs
2024-06-21 lots more 3d printing documentation
2024-06-21 3d printing now mostly documented
    [AN-1304-A-lid-machined.SLDDRW, AN-1304-A-lid-machined.SLDPRT, AN-1304-A-lid-machined.STEP, AN-1304-A-machined-box.SLDDRW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]
2024-06-21 arduino code directory name change
2024-07-23 knob added, perhaps erroneously
    [knob.SLDPRT, knob.STL]
2024-11-21 QNA is now the main repo that replaces "quantumswitch"
    [1.9in Coupler Module.stp, 1.9in Coupler Module.stp.SLDPRT, 10cm-chip-cal-board-1point2in.PcbDoc, 10cm-chip-cal-board-1point2in.PrjPcb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]
2024-11-22 24 line control panel designed
    [24line-control-panel.PcbDoc, 24line-control-panel.PrjPcb, 24line-control-panel.SchDoc]
2024-11-22 pcb work
    [1x9x1.PcbDoc, 24line-control-panel.PcbDoc, QNA-control-panel.PcbDoc, QNA-control-panel.PrjPcb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]
2024-11-22 main replication document and minor pcb edits
    [1x9x1.PcbDoc, 1x9x1.step]
2024-11-22 3d design and readme updates
    [1x9x1-mounting-bracket.SLDPRT, 1x9x1.SLDDRW, 1x9x1.SLDPRT, 1x9x1assembly.SLDASM]
2024-11-23 3d design update
    [HV-DCDC-bracket.SLDPRT, front-panel-edge-bracket.SLDDRW, front-panel-edge-bracket.SLDPRT, front-panel-edge-bracket.STL]
2024-11-23 building the documentation
    [HV-DCDC-bracket.SLDDRW, HV-DCDC-bracket.SLDPRT, HV-DCDC-bracket.STL]
2024-11-23 working on main readme scroll and powerpoint scroll
2024-11-24 documentation work
    [SP6T-COTS-BOM.xlsx, SP9T-Custom-BOM.xlsx]
2024-11-26 pcb layout work, details on 1x9x1
    [1x9x1.PcbDoc]
